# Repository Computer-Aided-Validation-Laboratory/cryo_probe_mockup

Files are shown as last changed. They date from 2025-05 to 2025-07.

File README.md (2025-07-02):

# Cryogenic Magnetic Probe Experimental Work

This repository contains work I have done in addition to taking experimental images of the mockup.
This includes:
- Error maps from DIC processing of images taken
- Python scripts to create these error maps from DIC data
- Python scripts to simulate the mock-up in Blender
- Blender generated images

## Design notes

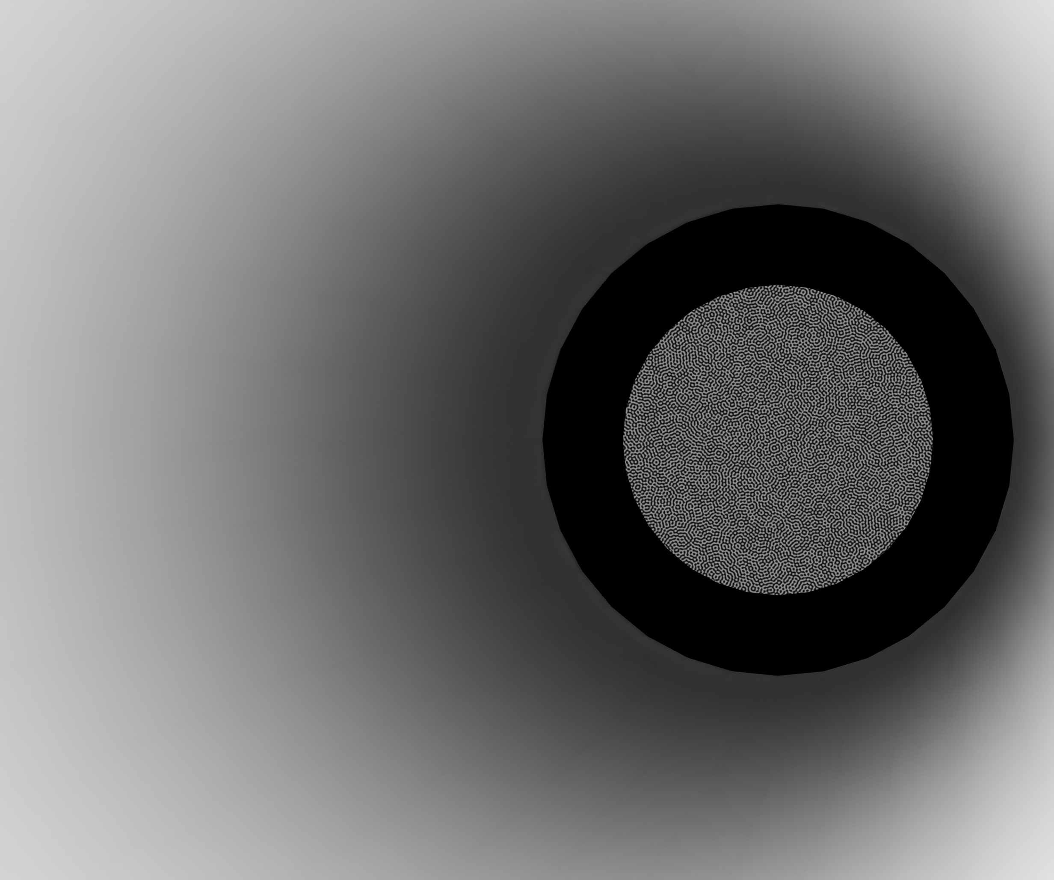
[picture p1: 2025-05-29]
blender_simulation/blenderimages/specified_locations/blenderimages/blenderimage_0_1.tiff

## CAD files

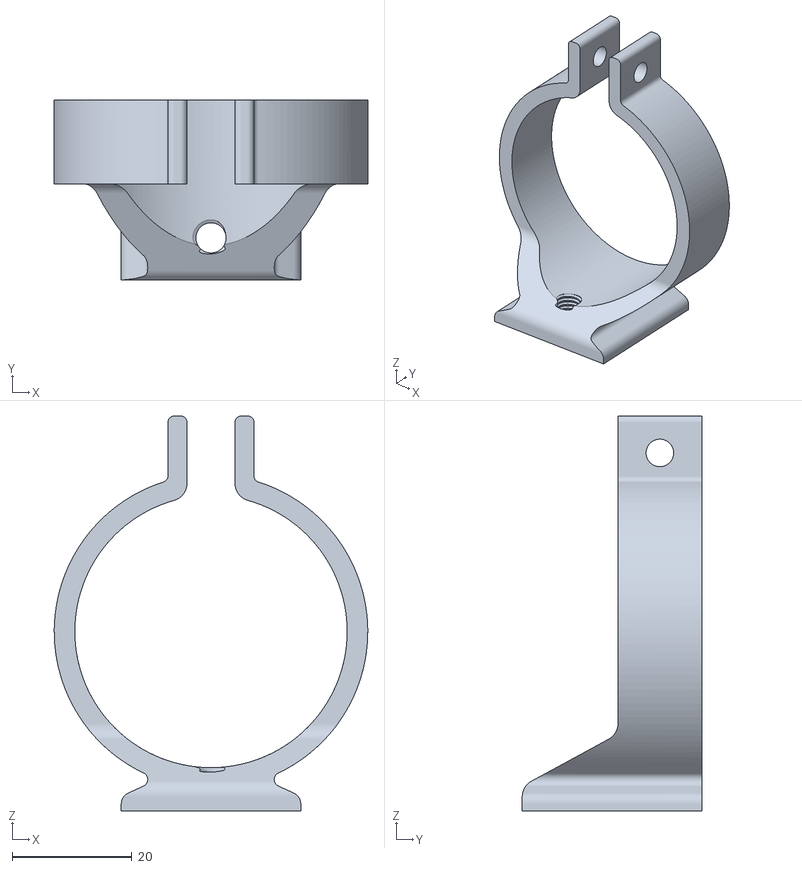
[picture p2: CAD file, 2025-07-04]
mock-up-supports/lens_support_74_shorter.stl
52.4 x 30.0 x 66.0

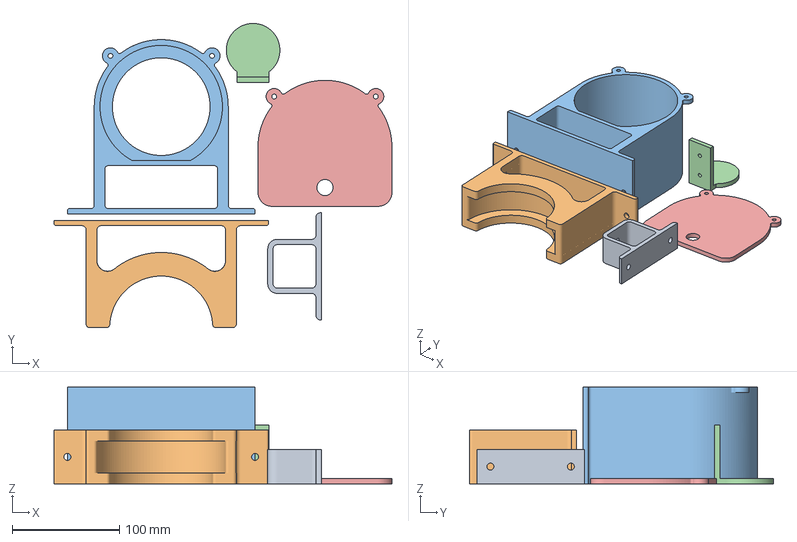
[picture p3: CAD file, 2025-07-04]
mock-up-supports/sample_supports.3mf.3mf
315.2 x 283.6 x 90.0 mm
cam_mount.stl
ring_light_mt.stl
sample_support1.stl
sample.stl
sample_support2.stl

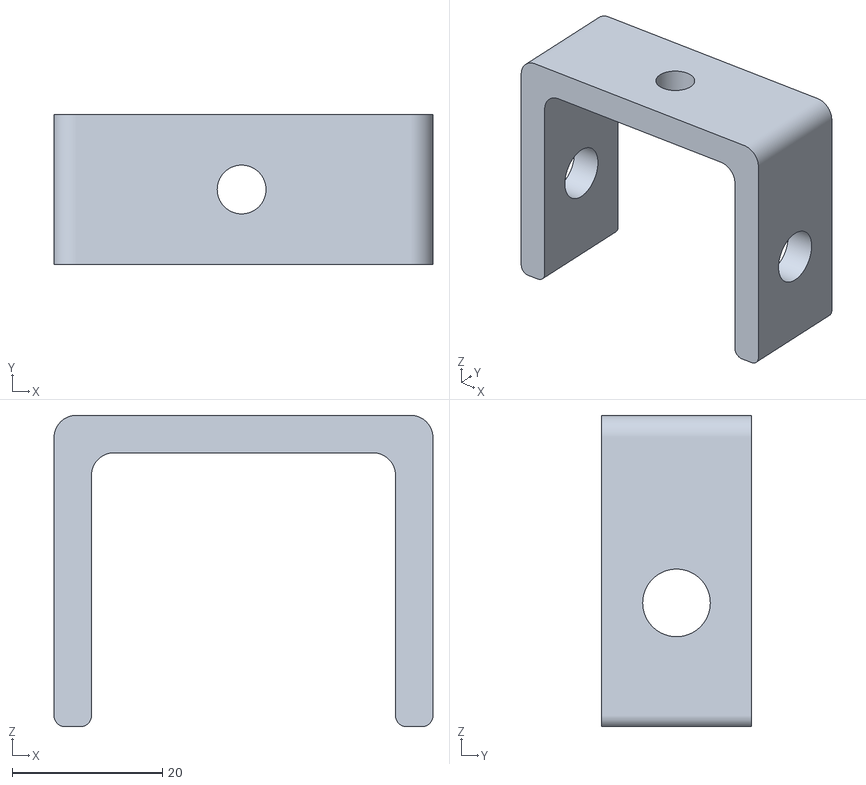
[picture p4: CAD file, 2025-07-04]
mock-up-supports/extrusion_lens_support.stl
50.5 x 20.0 x 41.5

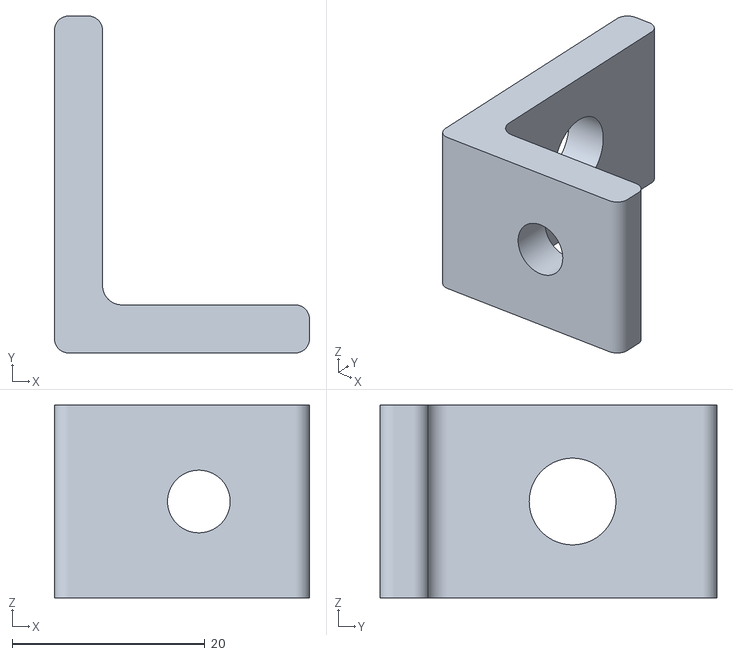
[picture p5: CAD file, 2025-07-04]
mock-up-supports/extrusion_table_support.stl
26.5 x 35.0 x 20.0

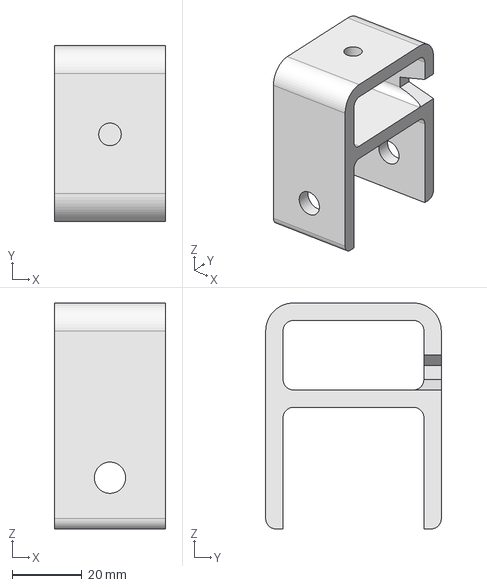
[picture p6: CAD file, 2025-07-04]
mock-up-supports/lens_mt_rail.FCStd
32.0 x 50.5 x 65.0 mm

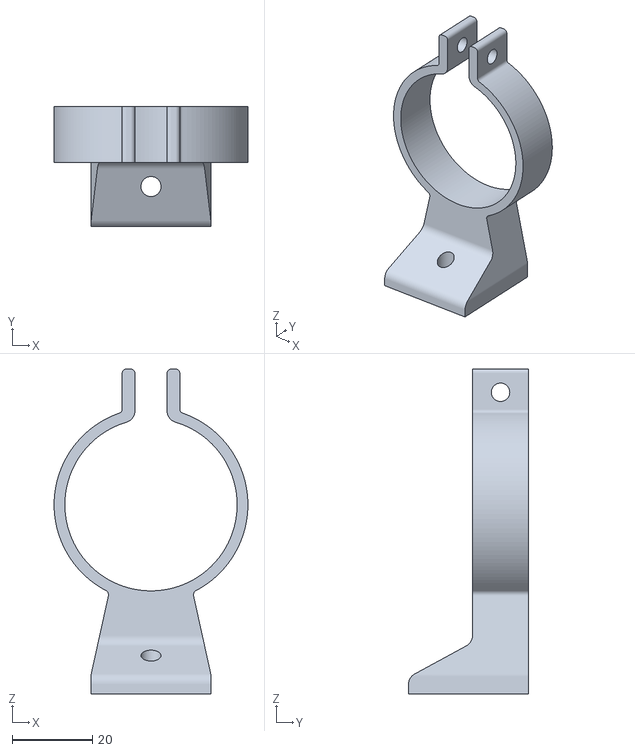
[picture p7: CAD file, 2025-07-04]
mock-up-supports/lens_support.stl
48.4 x 30.0 x 81.1

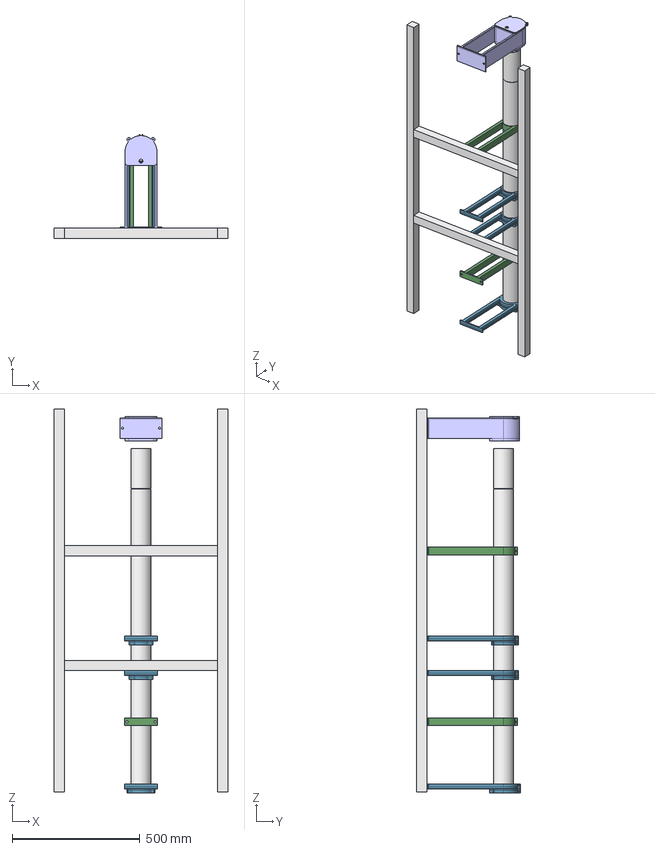
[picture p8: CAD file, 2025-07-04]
mock-up-supports/mock-up_vertical_setup.FCStd
680.0 x 406.1 x 1504.0 mm
w2_to_w3_pipe
w3_to_end
end_to_sample
top_to_w2
vertical002
vertical003
brace006
brace010
pipesupport001
pipesupport002
windowsupport001
windowsupport002
windowsupport003
windowsupport4
topwindow001
topwindow002
sample_support001
sample_support002

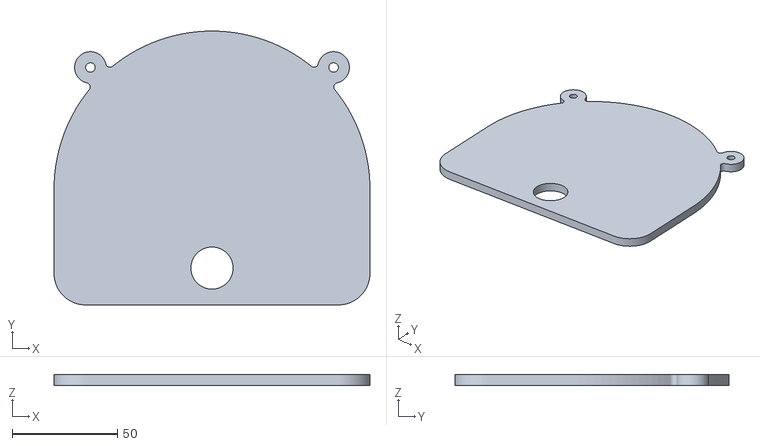
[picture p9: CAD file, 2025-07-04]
mock-up-supports/sample_support2.stl
150.0 x 130.0 x 5.00

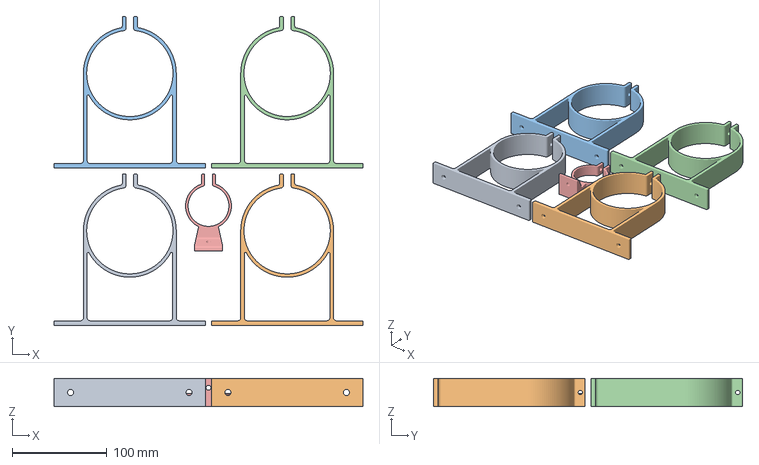
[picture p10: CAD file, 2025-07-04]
mock-up-supports/pipe_support.3mf
326.0 x 326.0 x 30.0 mm
pipe_support.stl
cam_lens_mt_75mm.stl

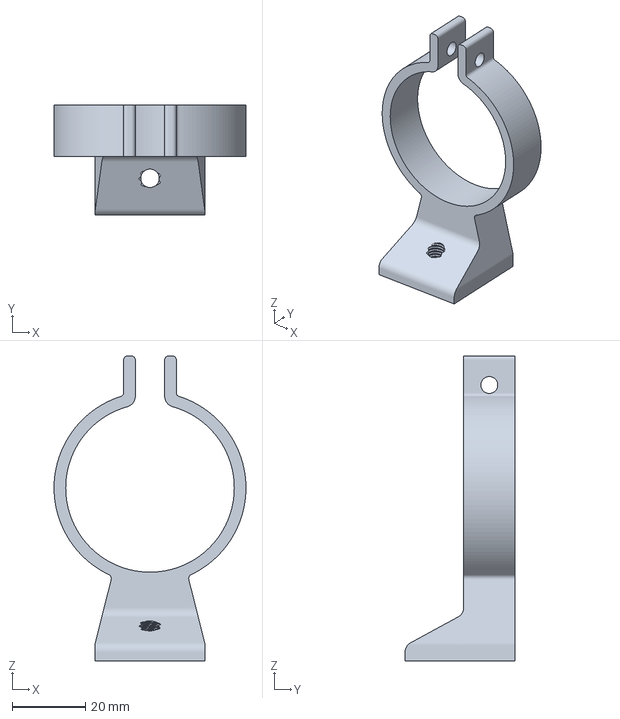
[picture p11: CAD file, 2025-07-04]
mock-up-supports/75_lens_support_threaded.3mf
52.4 x 30.0 x 83.3 mm

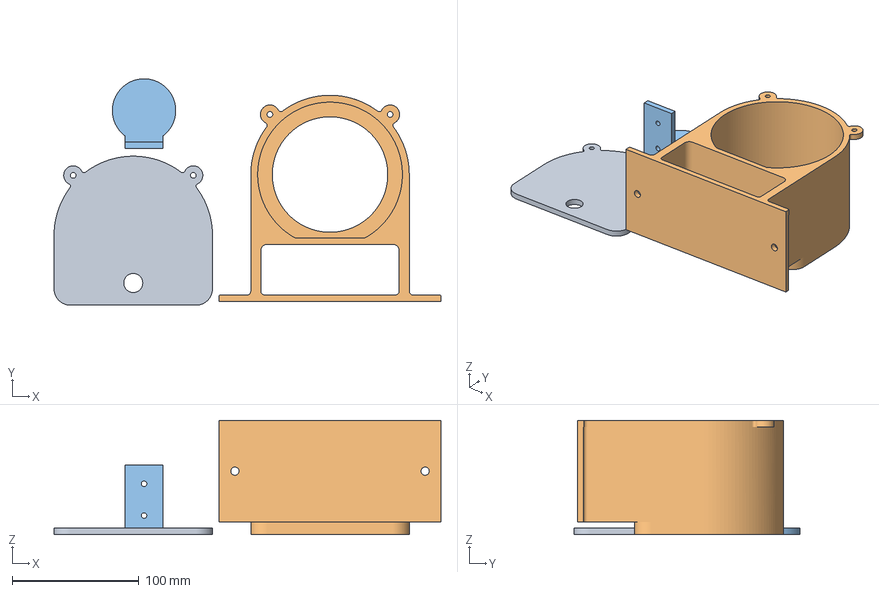
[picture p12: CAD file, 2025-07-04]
mock-up-supports/sample_supports.3mf
305.1 x 178.5 x 90.0 mm
sample_support2.stl
sample_support1.stl
sample.stl

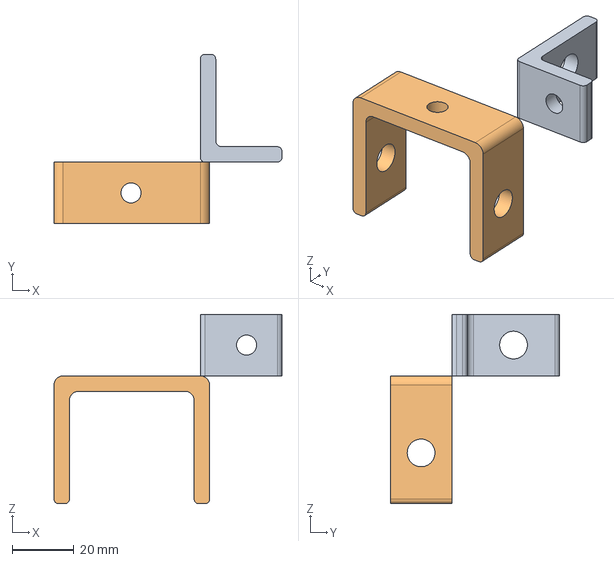
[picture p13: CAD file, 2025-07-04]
mock-up-supports/extrusion_supports.FCStd
74.0 x 55.0 x 61.5 mm
optical_table_support
lens_support

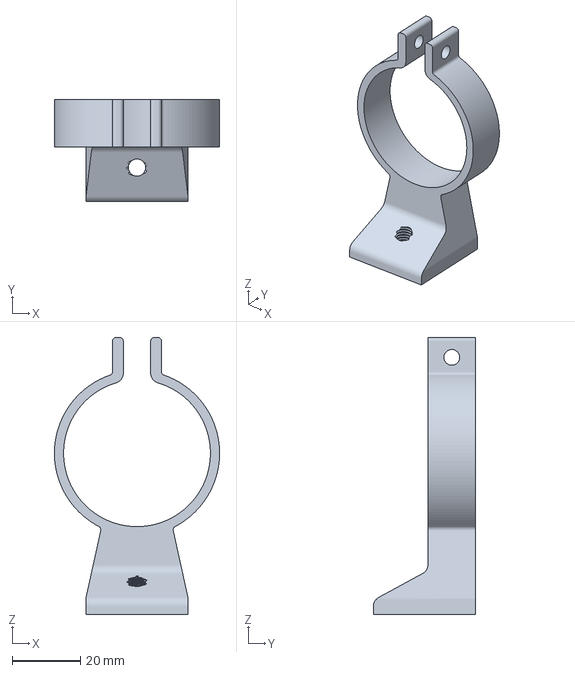
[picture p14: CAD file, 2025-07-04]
mock-up-supports/lens_support_75.3mf
48.4 x 30.0 x 81.1 mm

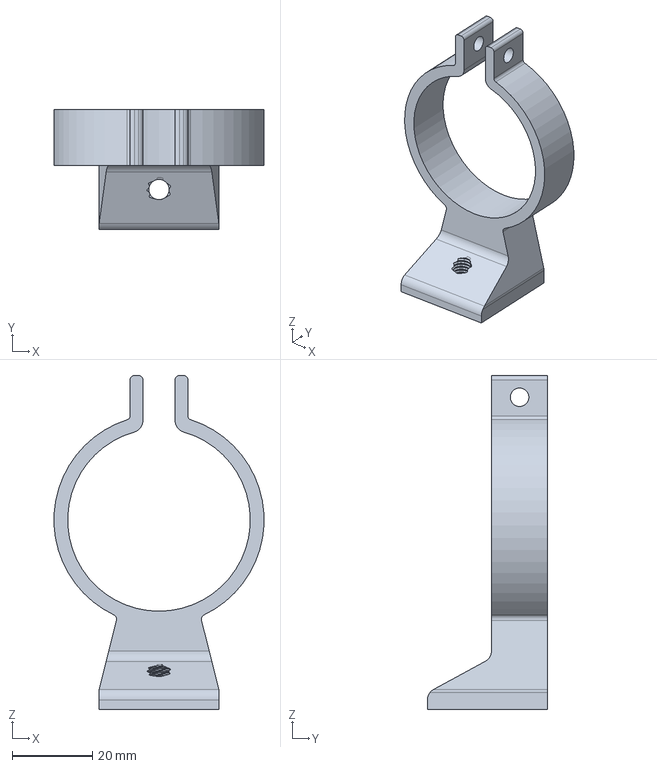
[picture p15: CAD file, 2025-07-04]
mock-up-supports/cam_lens_mt_75mm.FCStd
52.3 x 30.0 x 83.3 mm

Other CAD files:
mock-up-supports/lens_set_up.FCStd
mock-up-supports/cam_lens_mt_75mm_shorter.FCStd
mock-up-supports/cam_lens_mt_v2.FCStd
mock-up-supports/mock-up_horizontal_setup.FCStd
mock-up-supports/75_lens_support_threaded.stl
mock-up-supports/cam_lens_mt_75.FCStd
mock-up-supports/cam_lens_mt_75mm.3mf
mock-up-supports/cam_lens_mt_75mm.stl
mock-up-supports/cam_mount.stl
mock-up-supports/cam_single_mt_optical_table.FCStd
mock-up-supports/extrusion_optical_table_support.FCStd
mock-up-supports/len_mt_pad.FCStd
mock-up-supports/len_mt_pad.stl
mock-up-supports/lens_mt_rail.stl
mock-up-supports/lens_rail_mount.stl
mock-up-supports/lens_support_105.stl
mock-up-supports/mock-up_horizontal_setup-pipesupport001.3mf
mock-up-supports/pipe_initial_design.FCStd
mock-up-supports/pipe_support.stl
mock-up-supports/ring_light_mt.FCStd
mock-up-supports/ring_light_mt.stl
mock-up-supports/sampel_supports.3mf
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

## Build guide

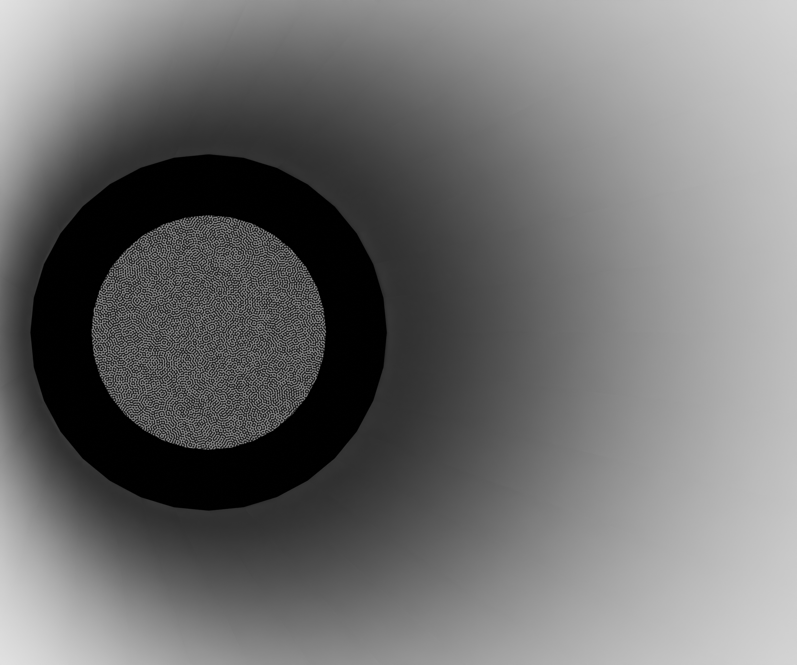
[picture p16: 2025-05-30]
blender_simulation/blenderimages/RBM/perfect_setup/blenderimages/blender_image_0_0_0.tiff

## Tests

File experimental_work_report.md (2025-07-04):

# Cryo-magnetic Probe Mock-up Work

## Summary of work undertaken
- 2D stereo setup used to test the light strength and suitability of the lenses.
- Stereo setup tested to see the suitability of a two camera stereo system and optimal camera and lighting placement was tested.
- 24 MPx cameras used to increase resolution, but hard to calibrate due to larger FOV.
- Correlation based optimisation investigated to improve out-of-plane measurements.
- Images taken down the mock-up with a stereo angle of 5 deg and images with an optimal stereo angle of 20 deg were compared.
- Setup simulated using Blender to evaluate uncertainty in the setup.

## Stereo Setup
Although having a stereo DIC setup is possible for this testing, it poses many challenges.
Most of the challenges were due to the constrained optical access present in the setup.
This impacted the lighting, lens choice and possible stereo angle.

The lighting in this setup was challenging since a powerful light source was required to illuminate the sample located ~1.4 m away.
It was decided to use a ring light to avoid shadows from the cameras.
This lighting then introduced another challenge: reflections from the probe itself.
In order to combat the effect of these reflections, polarising film was placed in front of the light and polarising filters were attatched to the lenses.
These polarisers greatly improved the quality of the images taken, and allowed them to be correlated through MatchID.
Another issue with the lighting was the difficulty in producing images where no part of the sample was over-exposed or in shadow.
This was possible with a smaller stereo angle between the cameras, but as the angle between the cameras increased this became a challenge and meant that MatchID struggled to correlate the images.
Even the images that were able to be correlated still had poor lighting, and could be improved by increased contrast in the speckle pattern. Therefore it would be good to investigate different lighting options.

The most challenging aspect of the setup was the positioning of the cameras.
Due to the long distance to the sample and the small diameter of the probe, the cameras had to be positioned fairly close to one another.
This meant that only a small stereo angle could be acheived.
This positioning constraint also impacted the choice of lenses to use.
Normally, high focal length macro lenses could be used for these scenarios with large stand-off distances.
However, since these lenses are considerably larger they could not be used for this application.
The size of lens was also a constraint of the stereo angle.

With the challenging camera setup came a challenging calibration.
Due to the fact that both cameras were looking down the probe and the end of the probe only took up a portion of their FOV, calibrating was not optimal.
Calibration images representative of the entire FOV could not be produced due to the optical setup.
This meant that the calibration parameters procuced from these calibration images are likely to not be fully accurate of reality.
Ways to try and mitigate this will be discussed below.

In order to mitigate the issues mentioned above, 100 mm fixed focal length lenses were used.
These were tested with both 24 MPx and 5 MPx cameras.
Since the 100 mm lenses are wider than the 75 mm lenses, they had to be moved further back to get an adequate stereo angle.
Due to the increased stand-off distance the setup with the 24 MPx cameras was difficult to calibrate, as the speckled area only made up around a third of the FOV.

Images of the mockup can be seen below:

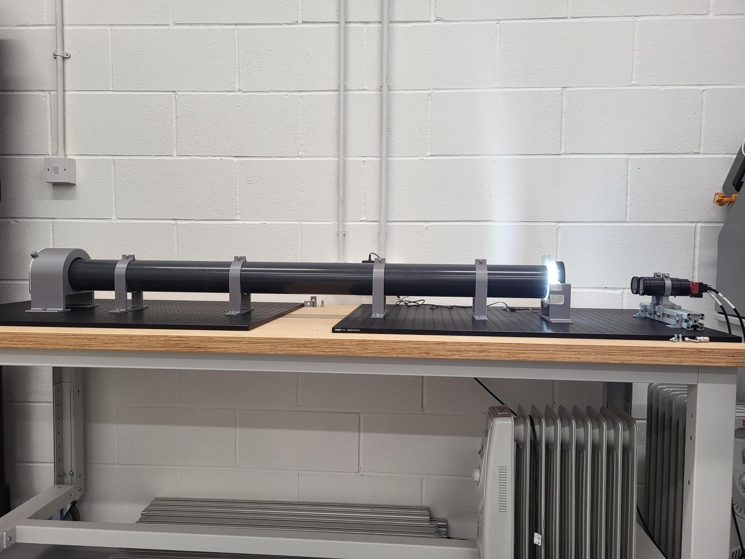
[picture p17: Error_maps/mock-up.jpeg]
Mock-up

_The mock-up with stereo DIC setup, with overall length = 193cm_

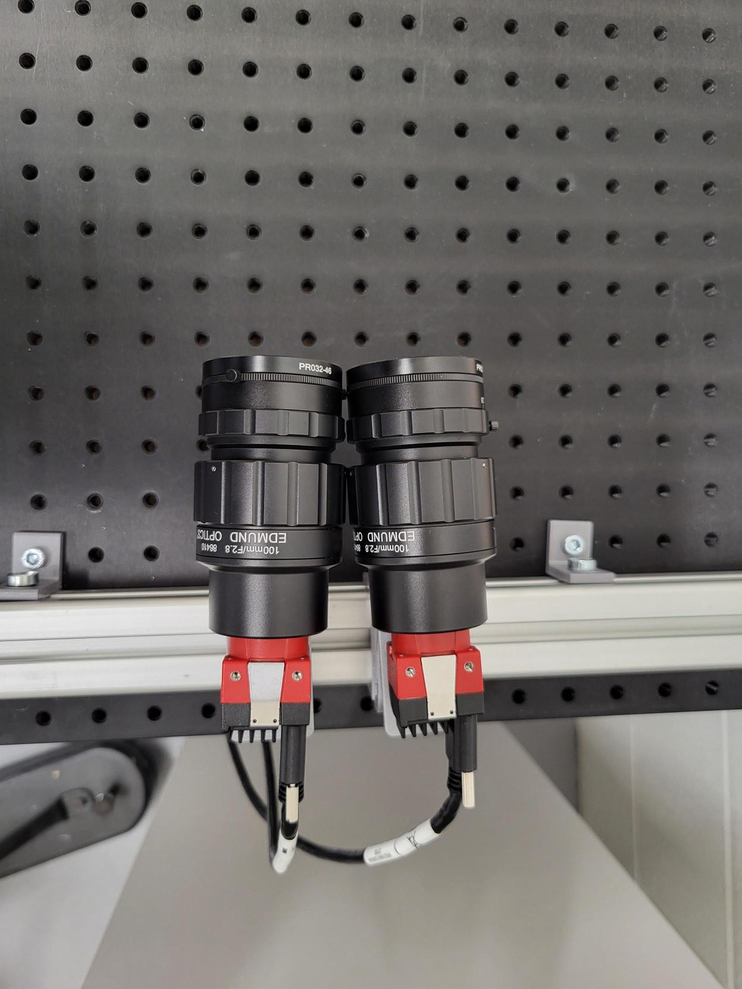
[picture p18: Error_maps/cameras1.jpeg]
Cameras1


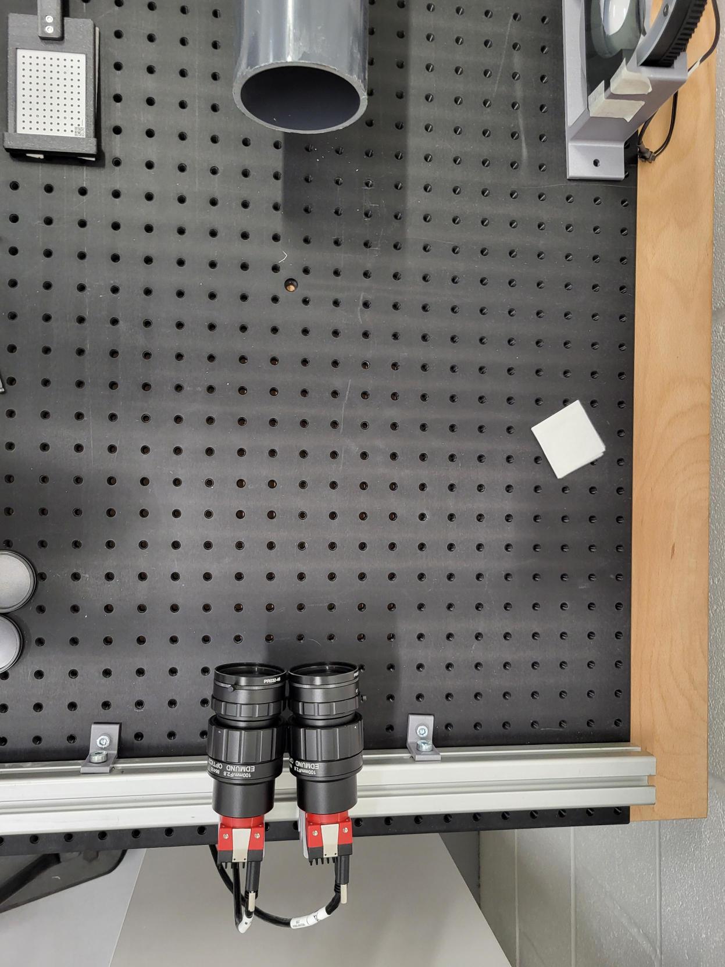
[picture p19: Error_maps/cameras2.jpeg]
Cameras2


## DIC Processing
### Correlation-based Optimisation
MatchID's correlation-based optimisation calibration method was tested on both experimental and Blender-rendered images.
This module can now input multiple stereo image pairs and minimise the epipolar distance to calculate a new set of calibration parameters.
There are three options for which calibration parameters to optimise:
- Extrinsics
- Extrinsics and intrinsics (exluding distortion)
- Extrinsics and intrinsics (including distortion)

The impact of all the options on the calibration parameters were investigated.
Generally, the intrinsic parameters did not change significantly, even when optimised.
Also when both intrinsic and extrinsic parameters were optimised, the extrinsic parameters did not change as significantly as when only the extrinsic parameters were optimised.

For all the sets of images tested, the stereo angle increased when the parameters were optimised.
This optimised calibration process has a positive impact on the processing of the DIC images.
Using the optimised calibration parameters lowers both the systematic and random error for both out-of-plane movement and epipolar distance.
The level of error for in-plane movement is increased, but ideal this error should be low enough that an increase will not be significant.
Both static and deforming/rigid body motion images can be utilised to optimise the calibration.

Optimisation for static images error maps
_Error maps comparing the impact of using correlation-based optimisation for static images_

Optimisation for rbm image error maps
_Error maps comparing the impact of using correlation-based optimisation for rigid body motion images_

### Image averaging
The impact of using image averaging on the noisefloor was investigated using a set of static images.
As can be seen below, image averaging improved the noisefloor so should be used for subsequent analysis.

Image averaging error maps

## Impact of Stereo Angle
The impact of the non-optimal stereo angle and reflections from the pipe were investigated.
This was done by comparing two setups:
- Imaging down the mock-up with a stereo angle of ~5 deg
- Imaging the sample at the same distance with an optimal stereo angle of ~20 deg

For each scenario, static and rigid body motion (both in and out of plane) images were taken.
For the rigid body motion images, the DIC calculated displacement was compared to the imposed displacement to obtain the error in the measurements.

This study showed the level of error present in the system associated with the cameras and lenses, not due to the reflection, lighting and stereo angle effects.

In plane rigid body motion error
_Error maps for the in plane rigid body motion images_

Out of plane rigid body motion error
_Error maps for the out of plane rigid body motion images_

Static images error
_Error maps for static images_

## Level of systematic and random error in the setup
### Static images
The error maps below show the systematic and random error for both in plane and out of plane displacement.
Two sets of static images were taken, so the results for both sets of images is shown.

Static images noisefloor

### Rigid body motion
Rigid body motion was carried out both in and out of plane to characterise the level of undertainty in the DIC measurements.
The difference between the imposed and calculated displacement was analysed.

Rigid body motion noisefloor

### 100 mm lenses setup
The 100 mm lenses were tested with both 5 MPx cameras and 25 MPx cameras.
Since the 100 mm lenses are wider than the 75 mm lenses, the cameras had to be moved further away from the sample to allow for both cameras to have a view of the sample.
This increased stand-off distance meant that the speckled area still only covered a small amount of the FOV of the 24 MPx camera.

The temporal noise in static images for both the 5 MPx and 24 MPx cameras with 100 mm lenses can be seen below:

100 mm lens noisefloor
_Error map showing the temporal noise for static images for both 5 MPx and 24 MPx cameras with 100 mm lenses_

## Comparison to Blender images
The setup was also simulated using Blender to investigate different experimental setups.
Through Blender it was seen that a face-on stereo would not be realistic due to the contrained optical access, so a symmetric approach was opted for instead.
Calibration and rigid body motion images rendered in Blender were also run through MatchID to assess the level of error present only due to the limited stereo angle.

It was found that the stereo angle calculated from the calibration images was lower than that of the system (3.53 deg compared to 5 deg).
Therefore, a level of systematic error will be present in the results due to the inaccurate calibration parameters.

## Recommended future work
### Impact of decrease in working distance
During testing, as the probe cools down it will contract. This will change the working distance between the sample and cameras.
This raises the question of whether the sample will remain in focus due to the camera's depth of field.
It may also be difficult to balance the depth of field and aperture, as lighting is also an issue in the setup.
With the current setup, the smallest aperture I have been able to use is f/4, as with smaller apertures the lighting is not strong enough to illumiate the sample sufficiently.

### Testing of calibration procedure
One method of calibrating the setup would be to calibrate the setup ex-situ, and then utilise the correlation-based optimisation module.
This module will use speckled images to correct the extrinsic parameters due to any slight changes to the setup.
This method could be investigated through calibrating the system, moving the camera setup slightly and then correcting for the calibration parameters.

### Different lighting methods
One difficulty with the stereo setup was positioning the ring light.
It was challenging to mititage the effects of overexposure from the light with poor lighting on the sample.
Therefore, it may be useful to experiment with different lighting scenarios e.g. behind the cameras to see if this can mitigate this issues.
A more powerful light will be required, as in order to gain better depth of field a smaller aperture will be required which needs better lighting, as mentioned above.

### Longer focal length lenses
One issue with the setup was the challenges in calibration.
This is due to the fact that the area visible at the end of the tube (including the speckled area) only takes up around half of the FOV.
This means that calibration images taken are only representative of part of the FOV, and therefore the calibration parameters calculated are not hugely accurate.
One way to mitigate this would be to use lenses with a higher focal length to get higher magnification.
This may in practice be challenging as higher focal length lenses will be larger, which will impact the stereo angle that can be acheived between the cameras.

### Higher resolution cameras
Two different cameras have been tested so far: 5 MPx and 24 MPx.
The setup with the 24 MPx camera was difficult to calibrate, due to the larger FOV.
However, the resolution of images from the 5 MPx cameras could be improved.
Therefore, it may be useful to investigate using a camera with a resolution between the two, to compromise between resolution and FOV size.

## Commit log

2025-05-29 Stereo calibration
2025-05-29 calibration moved
2025-05-30 MatchID calibration added
2025-05-30 Initial calibration images added
2025-06-11 Calibration with dof included
2025-06-11 calibration with dof
2025-07-04 cad files for mock-up added
    [75_lens_support_threaded.3mf, 75_lens_support_threaded.stl, cam_lens_mt_75.FCStd, cam_lens_mt_75mm.3mf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]
